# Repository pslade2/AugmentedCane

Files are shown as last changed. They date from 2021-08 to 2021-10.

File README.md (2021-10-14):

# AugmentedCane


The Augmented Cane project improves the mobility of people with impaired vision by using cutting-edge robotics. Read the full research paper: https://www.science.org/doi/10.1126/scirobotics.abg6594

If you use a part of this project please cite our work: P. Slade, A. Tambe, M. J. Kochenderfer, Multimodal sensing and intuitive steering assistance improve navigation and mobility for people with impaired vision. Sci. Robot. 6, eabg6594 (2021).

The Augmented Cane project is completely open-source. To build your own copy check out the cane_assembly document with instructions on replicating the device. The image of the Raspberry Pi used is available in a separate repository due to its size: https://doi.org/10.5281/zenodo.5508346

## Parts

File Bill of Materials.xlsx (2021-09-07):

Number | Part Name | Vendor | Quantity | Cost | Shipping | Total Cost | Link
1 | Raspberry Pi 4b+ (4 GB) | Adafruit | 1 | $55.00 | $0.00 | $55.00 | https://www.adafruit.com/product/4296
2 | RPLidar A1 | Amazon | 1 | $99.99 | $0.00 | $99.99 | https://www.amazon.com/Slamtec-RPLIDAR-Scanning-Avoidance-Navigation/dp/B07TJW5SXF?hvadid=385584089652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
3 | Motor | Pololu | 1 | $19.95 | $0.00 | $19.95 | https://www.pololu.com/product/3225
4 | GPS Breakout | Adafruit | 1 | $39.95 | $0.00 | $39.95 | https://www.adafruit.com/product/746
5 | NXP IMU | Adafruit | 1 | $14.95 | $0.00 | $14.95 | https://www.adafruit.com/product/3463
6 | RPi Camera | Adafruit | 1 | $29.95 | $0.00 | $29.95 | https://www.adafruit.com/product/3099
7 | RPi Camera Cable | Adafruit | 1 | $2.95 | $0.00 | $2.95 | https://www.adafruit.com/product/1731
8 | Pi Cobbler Breakout | Adafruit | 1 | $6.95 | $0.00 | $6.95 | https://www.adafruit.com/product/1754
9 | Protohat | Adafruit | 1 | $4.95 | $0.00 | $4.95 | https://www.adafruit.com/product/2310
10 | GPS Antenna | Adafruit | 1 | $14.95 | $0.00 | $14.95 | https://www.adafruit.com/product/960
11 | Micro SD Card | Amazon | 1 | $6.90 | $0.00 | $6.90 | https://www.amazon.com/Sandisk-Ultra-Micro-UHS-I-Adapter/dp/B073K14CVB?cv_ct_cx=16gb+sd&s=electronics
12 | LiPo Battery | Amazon | 1 | $13.00 | $0.00 | $13.00 | https://www.amazon.com/dp/B072PPRPRN
13 | LiPo Charger | Amazon | 1 | $12.00 | $0.00 | $12.00 | https://www.amazon.com/Blomiky-Charger-11-1V-Balance-Battery/dp/B072K5LHGM?s=toys-and-games
14 | USB cable | Adafruit | 1 | $2.95 | $0.00 | $2.95 | https://www.adafruit.com/product/4472
15 | Rechargeable Battery | Amazon | 1 | $12.50 | $0.00 | $12.50 | https://www.amazon.com/gp/product/B07MS1B8KQ/ref=ppx_yo_dt_b_asin_title_o07_s00?ie=UTF8&psc=1
17 | Motor Driver | Adafruit | 1 | $7.50 | $0.00 | $7.50 | https://www.adafruit.com/product/3190
18 | Pi Case | Amazon | 1 | $18.99 | $0.00 | $18.99 | https://www.amazon.com/Miuzei-Raspberry-HDMI-Micro-Aluminum-Included/dp/B07VX2WDHM
19 | White Cane | Amazon | 1 | $17.00 | $0.00 | $17.00 | https://www.amazon.com/Drive-Medical-Deluxe-Folding-Reflective/dp/B002VWK0HI
20 | Ear Buds | Amazon | 1 | $16.00 | $0.00 | $16.00 | https://www.amazon.com/iTeknic-Bluetooth-Waterproof-Earphones-Microphone/dp/B083Y19JTN
21 | 4mm shaft | Amazon | 1 | $7.99 | $0.00 | $7.99 | https://www.amazon.com/Sutemribor-100mm-Straight-Helicopter-Airplane/dp/B07FYTQWDC
22 | Omniwheel | Robotshop | 1 | $13.50 | $0.00 | $13.50 | https://www.robotshop.com/en/60mm-aluminum-omni-wheel.html
23 | Aluminum mounting hub | Robotshop | 2 | $6.21 | $0.00 | $12.42 | https://www.robotshop.com/en/4mm-aluminum-mounting-hub-60mm-omni-wheel.html
 |  |  |  |  | TOTAL: | $430.34

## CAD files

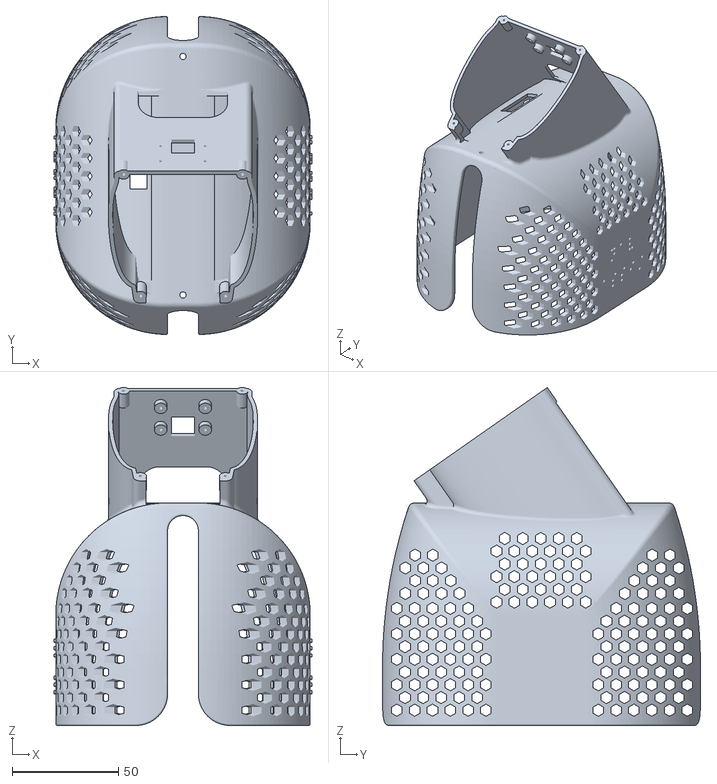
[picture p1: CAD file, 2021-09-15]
cane_hull.stl
121.6 x 150.0 x 159.4

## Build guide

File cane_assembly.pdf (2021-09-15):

Assembly instructions for the Augmented Cane:

See the components in the bill of materials listed in the repository to ensure you purchase the correct components.

Setting up software on the Raspberry Pi: The open-source software uses a Raspberry Pi image which can be downloaded from our repository. (https://doi.org/10.5281/zenodo.5508346) This image contains the operating system and code that will run on the Rasberry Pi. Once downloaded, unzip the image file (approximately 32 GB in size). Insert your microSD card into your computer using the SD card adapter. We will transfer the image to the microSD card using a free program called balenaEtcher. (https://www.balena.io/etcher/) Install this software and open it. Select the image location that you downloaded, select the microSD card as the drive to install to, and click “Flash!”. Once this has completed, you can eject the microSD card and insert it into the Raspberry Pi. You have finished installing the software and are ready to assemble the hardware.

Building the hardware:

1. To connect the camera to the Raspberry Pi, please see the Raspberry Pi Foundation instructions: https://projects.raspberrypi.org/en/projects/getting-started-with-picamera
2. To connect the RPLIDAR to the Raspberry Pi, simply plug the USB connector into the Raspberry Pi as shown in the image below.

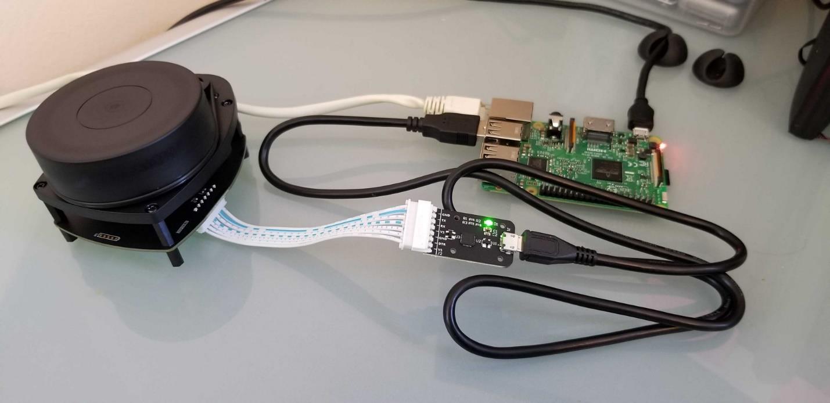
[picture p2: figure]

3. To connect the GPS breakout board to the Raspberry Pi, you will need to solder the VIN, GND, TX, RX pins on the GPS board to the 5V, GND, RX, TX pins on the Adafruit protohat board that will be connected to the Raspberry PI. The RX and TX should be connected to the opposite pins (RX is receive for GPS board, but TX (transmit) for the Pi). See example wiring info here: https://learn.adafruit.com/adafruit-ultimate-gps/circuitpython-parsing
a. To see an example of hot the protohat can be used with the Raspberry Pi, check out this Adafruit project: https://learn.adafruit.com/reef-pi-power-controller
4. To connect the IMU breakout board you will need to solder the VIN, GND, SCL, SDA pins on the IMU board to the 5V, GND, SCL, SDA pins on the Adafruit protohat.

5. The motor controller should be soldered following these instructions: https://learn.adafruit.com/adafruit-drv8871-brushed-dc-motor-driver-breakout/
a. Please note that the power for the motor will be supplied from the LiPo battery on the bill of materials. DO NOT DIRECTLY SOLDER THE BATTERY TO THE POWER PINS. Solder a connector to the power pins so the battery can be disconnected.
6. The pushbutton used to turn off the motor during operation (option for use) should have one end soldered to the #18 pin on the Adafruit protohat and the other pin soldered to 3.3V.
7. The Raspberry Pi will be powered by the rechargeable battery connected into the Raspberry Pi USB-C port.
8. The Raspberry Pi should be protected with the provided case in the bill of materials. The cobbler breakout allows the Adafruit protohat board to be attached to the Raspberry Pi while it is in the case. For attaching all the sensors to the cane you can 3D print the shell housing (STL file in the repository) either with a local 3D printer or using an online service such as Protolabs. (https://www.protolabs.com/) I have uploaded the shell file to Shapeways to make it easy to order directly to your house: https://www.shapeways.com/product/CSHCYNAWM/augmented-cane-3d-printed-shell
a. The components that do not mount to the 3D printed shell (batteries, etc) can be attached to the Raspberry Pi case inside the shell with tape or Velcro. I’ve attached additional images of the assembly to help with this process.

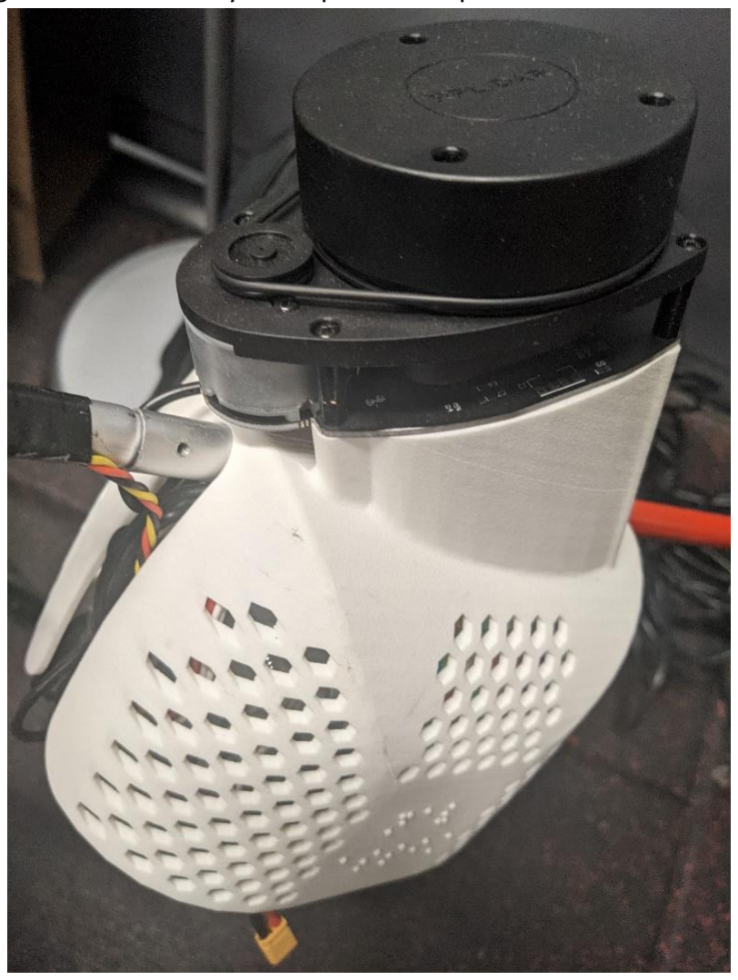
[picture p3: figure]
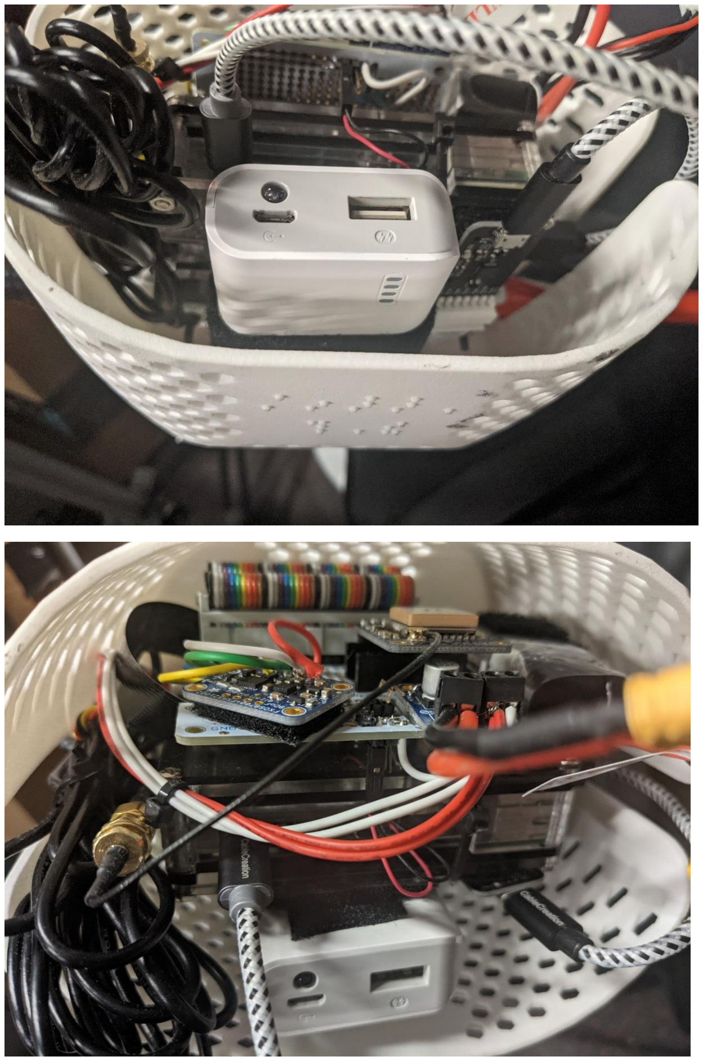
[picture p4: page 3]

9. Assembling the omniwheel and motor assembly will require a hand drill. Drill a hole in the end of the cane. Assemble the motor, two aluminum mounting hubs, omniwheel, and 4mm shaft as shown in the image below.

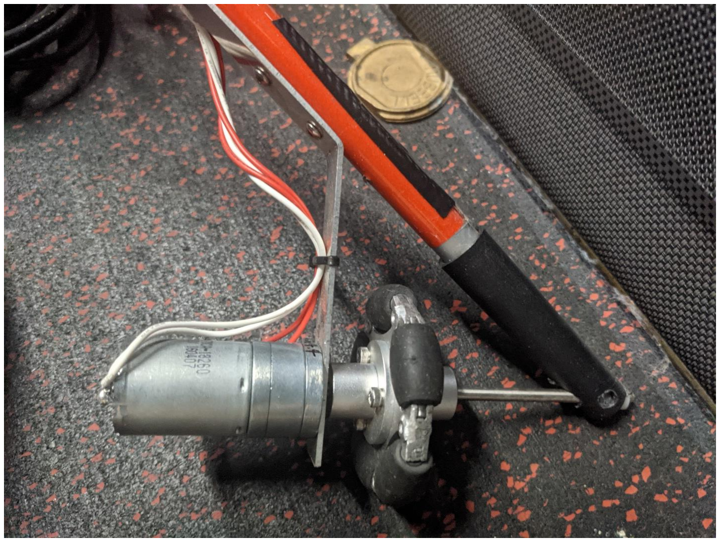
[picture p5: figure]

10. You can run the different programs already installed by using the command line to navigate to the correct directory and entering the following commands:
a. sudo python3 obstacle_avoidance.py
b. sudo python3 gps_navigation.py

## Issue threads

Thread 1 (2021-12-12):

### ISSUE TITLE
System startup problems

### ISSUE THREAD

**Issue by wangjie0323** [pslade2/AugmentedCane#1]
![raspi](https://user-images.githubusercontent.com/52735784/143732383-4849a401-8698-48b2-a1f2-975d86f5b2d3.jpg)

What is the reason why I can't enter the system using the image you provided?

**Comment by pslade2** [comment]
Hi, this happens when a newer raspberry pi board is made, it has slightly different software. You can either use a fresh install of the raspberry pi operating system and download the code repository from here (you'll have to install dependencies). Or you can change a few files in the system image I provided for you board (instructions on how to do that here: https://raspberrypi.stackexchange.com/questions/127325/raspberry-pi-not-booting-recover4-elf-is-not-compatible).

**Comment by kenpower** [comment]
I had the same problem, but copying the start4*.elf files (as suggested in the SE answer) from a newer image did not help.

How do I find out what dependencies we need?

**Comment by pslade2** [comment]
Hi Ken. Did you make sure to copy the start4.elf files for you specific raspberry pi version? I've had success updating it for several different models of pi.

Otherwise I would suggest getting the latest Raspbian Image (I used a 2019 raspbian image) and installing the python dependencies for whichever script you are trying to run. Let me know if you have more questions!

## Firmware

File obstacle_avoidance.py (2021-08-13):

## TODO: try and make less brittle by using more sections of lidar for just slight turns rather than whole 90 degree turns
## use more sections on the right to improve stability of shorelining, i.e. doorways cause big issues right now

#!/usr/bin/env python3
# to run on raspberry pi use, add sudo if run into issues with serial: python3 assist_cane_hallway_test.py
from rplidar import RPLidar
import RPi.GPIO as IO
import numpy as np
import time
import serial
import struct
import signal
import sys
import board
import busio
import adafruit_fxos8700 # accel and magnetometer
# import adafruit_fxas21002c # currently don't need gyro
import cane_functions as cf

# stops the motors  called when ctrl-c is hit
def exit_function(signal, frame):
    print('Exiting...')
    p_L.stop()
    p_R.stop()
    lidar.stop()
    lidar.stop_motor()
    time.sleep(2.0)
    lidar.disconnect()
    time.sleep(2.0)
    sys.exit(0)
# intialize exit function
signal.signal(signal.SIGINT, exit_function)

# intialize serial and rplidar
PORT_NAME = '/dev/ttyUSB0'
run_flag = True # starts the program, keeps it running
time.sleep(.5) # rest to start serial
lidar = RPLidar(PORT_NAME)
iterator = lidar.iter_scans(max_buf_meas=120)
time.sleep(.5) # pause to start lidar scanning

# distance and lidar thresholds
hallway_steering_thresh = 950.0 # if any lidar reading less than this, move away from that side
forward_thresh = 1850.0 # only look to turn if less than 2 meters of room ahead
right_thresh = 900.0 # keep the right wall 1m away at all times
right_check_thresh = 2000.0 # always turn right if at least this much space
crash_thresh = 400.0 # if turning into a wall then stop turning
angle_offset = 0.0 #-45.0 # because lidar turned 45 degrees to left
forward_range_low = -5.0+angle_offset # in degrees
forward_range_upper = 5.0+angle_offset # in degrees
left_range_low = 85.0+angle_offset #in degrees
left_range_upper = 95.0+angle_offset #in degrees
right_range_low = -95.0+angle_offset #in degrees
right_range_upper = -85.0+angle_offset #in degrees

# discretized lidar array setup
array_sections = 19 # always have odd value here
num_front_sect = 2 # use the middle section +/- this many sections for checking front collision
array_start = -90.0
array_stop = 90.0
arr_width = (array_stop - array_start)/array_sections
lidar_ang_arr = np.zeros((array_sections,2)) # start then stop angle values
lidar_arr_mean = np.zeros(array_sections) # goes from right to left
distances = np.zeros(array_sections)
for i in range(array_sections):
    start_ang = array_start+i*arr_width
    stop_ang = start_ang + arr_width
    lidar_arr_mean[i] = int((start_ang + stop_ang)/2.0)
    lidar_ang_arr[i,:] = [start_ang+angle_offset,stop_ang+angle_offset]
mid_ind = array_sections//2
lidar_arr_mean -= lidar_arr_mean[mid_ind]
lidar_arr_mean = -1*lidar_arr_mean

# define motor pins, initialize, and constants
IO.setwarnings(False)
IO.setmode (IO.BCM)
m_pin_R = 12
m_pin_L = 13
pwm_freq = 100
IO.setup(m_pin_L,IO.OUT)
IO.setup(m_pin_R,IO.OUT)
p_L = IO.PWM(m_pin_L,pwm_freq)
p_R = IO.PWM(m_pin_R,pwm_freq)
p_L.start(0)
p_R.start(0)
motor_gain = 0.43 # for angles, 0.035 for based on distance
hallway_bump_gain = 0.15
motor_max = 60 # max speed
motor_min = 20 # min speed where motion occurs w/ friction
motor_command = 1
m_avg = 25 # parameters for sweeping
m_amp = 25
m_per = 1.5
m_bias = 0.0
m_offset = 2.4 # scalar to speed up obstacle avoidance

# defining pushbutton GPIO
button_pin = 18
IO.setup(button_pin, IO.IN)
if cf.read_pushbutton(button_pin): # if not holding button on startup
    engage_sweep = True
else:
    engage_sweep = False

# defining imu setup and constants
i2c = busio.I2C(board.SCL, board.SDA)
fxos = adafruit_fxos8700.FXOS8700(i2c)
# fxas = adafruit_fxas21002c.FXAS21002C(i2c)
dec_angle = -13.0 # update based on month (or use gps info)!
d2r = 3.14159/180.0 # degrees to radians
r2d = 1.0/d2r # radians to degrees
offset_vec = np.array([-31.85, -9.2, 534.15]) # correcting error in magnetometer
scale_vec = np.array([0.9871977, 0.97198879, 1.04360902]) # correcting error in magnetometer
loop_num = 20 # how many loops before print state info
deg_turn = 65.0 # degrees to turn left or right
turn_threshold = 10.0 # range of degrees (+/-) within to stop turning
lidar_gain = 0.98 # NOT USED RN: multiplier raised to the power of distance intervals, to prevent accidental Turning

# GPS placeholder
target_heading = 0.0
current_heading = 0.0
deadband = 0

# audio state toggle
playing_audio = False # start this way
prev_pa_flag = False
audio_start_time = time.time()
audio_delay = 2.3 # time in seconds between audio allowed to play

### Initializing state variables
while(run_flag):
    # stop motors and check reset button
    p_L.ChangeDutyCycle(0) # zero motors
    p_R.ChangeDutyCycle(0)
    button_state = cf.read_pushbutton(button_pin)
    time.sleep(0.1)
    # restart time values
    loop_time = time.time()
    loop_cnt = 0
    # state machine values
    forward_distance = 0.0
    left_distance = 0.0
    right_distance = 0.0
    goal_yaw = 0.0
    cur_yaw = 0.0
    state = 1

    ### Continually run code for hallway tracking
    while(button_state): # run until reset button pushed
        ## UPDATE CUR_YAW WITH IMU
        cur_yaw = cf.readCompass(dec_angle, offset_vec, scale_vec, fxos.magnetometer, r2d)
        ## READ AND UPDATE LIDAR
        lidar_scan = next(iterator)
        distances = cf.compute_lidar_array(lidar_scan, lidar_ang_arr, distances)
        if distances[mid_ind] > 0: # check if lidar readings initialized
            ## CHECK STATE MACHINE
            playing_audio, motor_command = cf.obstacle_state_machine(playing_audio, distances, mid_ind, m_offset, motor_gain, motor_max, deadband, target_heading, current_heading, motor_min, lidar_arr_mean, forward_thresh)
            ## CHECK WHEN TO ALLOW AUDIO AGAIN
            playing_audio, prev_pa_flag, audio_start_time = cf.wait_audio(playing_audio, prev_pa_flag, audio_start_time, audio_delay)
            if motor_command == 0 and engage_sweep: ## CHECK SWEEPING
                motor_command = cf.sweep_sine(m_avg, m_amp, m_bias, m_per)
        ## UPDATE MOTOR COMMAND
        cf.update_motors(motor_command, p_L, p_R)
        ## CHECK RESET BUTTON
        button_state = cf.read_pushbutton(button_pin)
        ## PRINT STATE INFORMATION
        loop_cnt += 1
        if loop_cnt % loop_num == 0: # print how fast it is running
            loop_delay = (time.time() - loop_time)/loop_num
            print(np.round(distances[4:-4],0))
            print(np.round(lidar_arr_mean[4:-4],1))
            print("state:",state, ' ', "goal yaw:", goal_yaw, ' ', "cur yaw:",cur_yaw, ' ', "fwd:",round(distances[mid_ind]), ' ', "Min:", round(np.amin(distances)),' ', "Min ind:",np.argmin(distances)-mid_ind,' ','Mot:',motor_command)
            # print("Loop is running at: ", round(loop_delay,3), " seconds or ", round(1.0/loop_delay,1), "hz")
            loop_time = time.time()

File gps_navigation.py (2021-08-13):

### TODO add a function to see if actually closer to further point than current waypoint and skip to that one.
import time
import adafruit_gps
import serial
import signal
import numpy as np
import board
import busio
import adafruit_fxos8700
#import adafruit_fxas21002c
import RPi.GPIO as IO
import cane_functions as cf
from rplidar import RPLidar
import os
import sys
import gpxpy
import gpxpy.gpx

# stops the motors  called when ctrl-c is hit
def exit_function(signal, frame):
    print('Exiting...')
    p_L.stop()
    p_R.stop()
    lidar.stop()
    lidar.stop_motor()
    time.sleep(2.0)
    lidar.disconnect()
    time.sleep(2.0)
    sys.exit(0)
# intialize exit function
signal.signal(signal.SIGINT, exit_function)
obstacle_det = True
audio_feedback = int(sys.argv[2])
compass_correct = 6.0 # add on to improve compass heading estimates
audio_ang_offset = 90.0

if audio_feedback:
    print("Starting audio feedback mode")


# initialize the saving folder
subj = str(sys.argv[1])
save_dir = os.getcwd() + '/gps_data/' + subj# + '/'# + str(run_num)
try:
    os.mkdir(save_dir)
except:
    print("Save dir exists: ", save_dir)
files = os.listdir(save_dir)
run_num = len(files)+1
save_dir = save_dir + '/' + str(run_num) + '/'
os.mkdir(save_dir)

# load the gps data as a list
#gps_file = os.getcwd() + '/gps_data/gpx/test_path.gpx' #path1.gpx'
#gpx_f = open(gps_file, 'r')
#gpx = gpxpy.parse(gpx_f)
#points = gpx.tracks[0].segments[0].points
#waypoint_list = []
#for p in points:
#    waypoint_list.append([p.latitude, p.longitude])
#waypoint_list = np.load(os.getcwd() + '/gps_data/gpx/path' + str(sys.argv[3]) + '.npy')
#waypoint_list = cf.load_waypts('GPS','3')#'SXX','31')
waypoint_list = np.load(os.getcwd() + '/gps_data/path2.npy')

uart = serial.Serial("/dev/ttyS0", baudrate=9600, timeout=10)
gps = adafruit_gps.GPS(uart, debug=False)     # Use UART/pyserial
# Turn on the basic GGA and RMC info (what you typically want)
gps.send_command(b'PMTK314,0,1,0,1,0,0,0,0,0,0,0,0,0,0,0,0,0,0,0')
gps.send_command(b'PMTK220,1000') # Set update rate to once a second.
# Main loop runs forever printing the location, etc. every second.
last_print = time.monotonic()

# intialize serial and rplidar
PORT_NAME = '/dev/ttyUSB0'
run_flag = True # starts the program, keeps it running
time.sleep(.5) # rest to start serial
if not audio_feedback:
    lidar = RPLidar(PORT_NAME)
    iterator = lidar.iter_scans(max_buf_meas=120)
time.sleep(.5) # pause to start lidar scanning

# initialize the gps settings
d2r = 3.14159/180.0 # degrees to radians
r2d = 1.0/d2r # radians to degrees
initialized = False
main_rate = 1.0 # rate in hz
dec_angle = 0.0 # declination angle https://www.pveducation.org/pvcdrom/properties-of-sunlight/declination-angle
waypoint_dist_tolerance = 5 # tolerance in meter to waypoint; once within this tolerance, we'll advance to the nect waypoint
heading_tolerance = 10 # tolerance +/- (in degrees) within which we don't attempt to turn to intercept targetHeading
# waypoints lat/long in degree decimal
#waypoint_list = [[37.426995365893596,-122.17254054883],[37.42721666379759,-122.1724720452093],[37.42757960628986, -122.17234587409479]]
number_waypoints = len(waypoint_list)
waypnt_cnt = 0
cur_waypoint = waypoint_list[waypnt_cnt]
reached_last_waypoint = False
# GPS heading is 0 deg at N, with  0 --> 360 going clockwise from 12 to 12

target_heading = 0.0
cur_heading = 0.0
comp_heading = 0.0
head_vec = np.zeros(5)
deadband = 6 # within +/- degrees for compass to turn off

# setup the imu settings
i2c = busio.I2C(board.SCL, board.SDA)
fxos = adafruit_fxos8700.FXOS8700(i2c)
#acc = adafruit_fxos8700.FXAS21002C(i2c)
time.sleep(0.5)
offset_vec = np.array([-26.0,1.0,541.15])#[-31.85, -9.2, 534.15])
scale_vec = np.array([1.0264612954186412,0.9668898809523808,1.008537058595266])#[0.9871977, 0.97198879, 1.04360902])
#fxas = adafruit_fxas21002c.FXAS21002C(i2c)

# parameters for lidar
forward_thresh = 1700.0 # only look to turn if less than 2 meters of room ahead
angle_offset = 0.0 # because lidar turned 45 degrees to left

# discretized lidar array setup
array_sections = 19 # always have odd value here
num_front_sect = 3 # use the middle section +/- this many sections for checking front collision
array_start = -90.0
array_stop = 90.0
arr_width = (array_stop - array_start)/array_sections
lidar_ang_arr = np.zeros((array_sections,2)) # start then stop angle values
lidar_arr_mean = np.zeros(array_sections) # goes from right to left
distances = np.ones(array_sections)*3000.0
for i in range(array_sections):
    start_ang = array_start+i*arr_width
    stop_ang = start_ang + arr_width
    lidar_arr_mean[i] = int((start_ang + stop_ang)/2.0)
    lidar_ang_arr[i,:] = [start_ang+angle_offset,stop_ang+angle_offset]
mid_ind = array_sections//2
lidar_arr_mean -= lidar_arr_mean[mid_ind]
lidar_arr_mean = -1*lidar_arr_mean

# setup the motor specs
IO.setwarnings(False)
IO.setmode (IO.BCM)
m_pin_R = 12
m_pin_L = 13
pwm_freq = 100
IO.setup(m_pin_L,IO.OUT)
IO.setup(m_pin_R,IO.OUT)
p_L = IO.PWM(m_pin_L,pwm_freq)
p_R = IO.PWM(m_pin_R,pwm_freq)
p_L.start(0)
p_R.start(0)
motor_max = 60
motor_min = 20
motor_gain = 0.43 # approx 80 degree error to kick max motor = (35/80)
motor_command = 1
m_avg = 25 # parameters for sweeping
m_amp = 25
m_per = 1.5
m_bias = 0.0
m_offset = 2.4 # scalar to speed up obstacle avoidance

# defining pushbutton GPIO
button_pin = 18
IO.setup(button_pin, IO.IN)
button_state = True
if cf.read_pushbutton(button_pin): # if not holding button on startup
    engage_sweep = True
else:
    engage_sweep = False
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

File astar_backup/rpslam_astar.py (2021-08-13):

#!/usr/bin/env python3

'''
rpslam.py : BreezySLAM Python with SLAMTECH RP A1 Lidar
                 
Copyright (C) 2018 Simon D. Levy

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
You should have received a copy of the GNU Lesser General Public License 
along with this code.  If not, see <http://www.gnu.org/licenses/>.
'''

MAP_SIZE_PIXELS         = 500
MAP_SIZE_METERS         = 10
LIDAR_DEVICE            = '/dev/ttyUSB0'


# Ideally we could use all 250 or so samples that the RPLidar delivers in one 
# scan, but on slower computers you'll get an empty map and unchanging position
# at that rate.
MIN_SAMPLES   = 20

from breezyslam.algorithms import RMHC_SLAM
from breezyslam.sensors import RPLidarA1 as LaserModel
from rplidar import RPLidar as Lidar
try:
    from roboviz import MapVisualizer
    headless = False
except:
    headless = True
import astar_funct as af
import numpy as np
import cane_functions as cf
import os
import RPi.GPIO as IO
import signal
from picamera import PiCamera
import time
import sys
import warnings

def exit_function(signal, frame):
    print('Exiting...')
    p_L.stop()
    p_R.stop()
    lidar.stop()
    lidar.stop_motor()
    time.sleep(2.0)
    lidar.disconnect()
    time.sleep(2.0)
    sys.exit(0)

if __name__ == '__main__':
    # intialize exit function
    signal.signal(signal.SIGINT, exit_function)
    warnings.filterwarnings("ignore")
    # Connect to Lidar unit
    lidar = Lidar(LIDAR_DEVICE)

    # Create an RMHC SLAM object with a laser model and optional robot model
    slam = RMHC_SLAM(LaserModel(), MAP_SIZE_PIXELS, MAP_SIZE_METERS)
    # Set up a SLAM display
    if not headless:
        viz = MapVisualizer(MAP_SIZE_PIXELS, MAP_SIZE_METERS, 'SLAM')
    # Initialize an empty trajectory
    trajectory = []
    # Initialize empty map
    mapbytes = bytearray(MAP_SIZE_PIXELS * MAP_SIZE_PIXELS)
    # Create an iterator to collect scan data from the RPLidar
    iterator = lidar.iter_scans()

    # We will use these to store previous scan in case current scan is inadequate
    previous_distances = None
    previous_angles    = None
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

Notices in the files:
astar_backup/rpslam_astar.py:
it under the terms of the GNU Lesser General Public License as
